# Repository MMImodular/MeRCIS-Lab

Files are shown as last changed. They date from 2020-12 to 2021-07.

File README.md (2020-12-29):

# MeRCIS Lab
##### Contributors: Matt Gaines, Joe Cressman, Jason Paximadas
___
This repository will be used to keep files up to date without dealing with Google Drive permissions.
The primary use case for now is maintaining a standard Eagle Library for future designs, but more will appear in time.

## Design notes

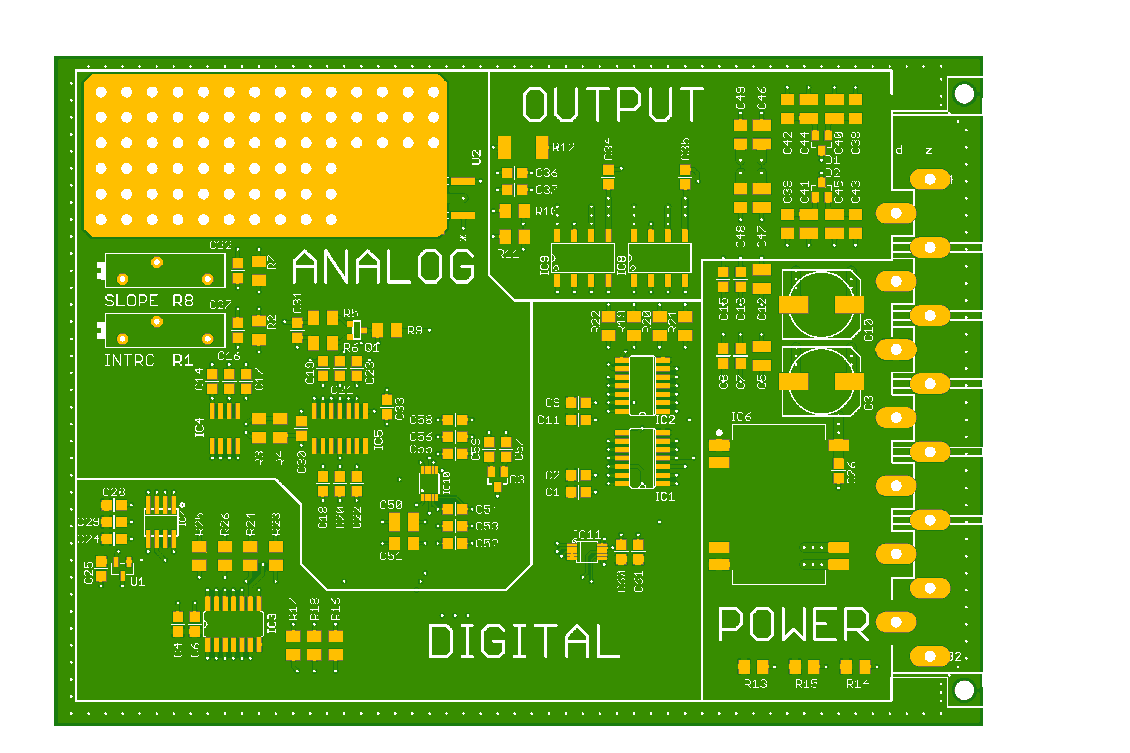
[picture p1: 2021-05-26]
Rev P/Transconductance Card222.png

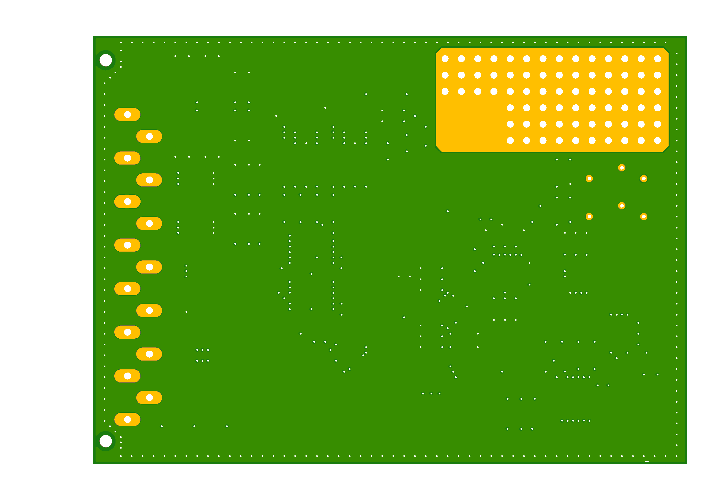
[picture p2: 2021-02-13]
Rev P/Transconductance Card Bottom.png

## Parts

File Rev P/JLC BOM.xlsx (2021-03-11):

Comment | Designator | Footprint | LCSC Part # | Column1
AD5551 | IC7 | SO-8 |  | pads good
0.01u | C14, C22, C23, C31, C33, C54, C58 | C0805 | C1710 (https://lcsc.com/product-detail/Multilayer-Ceramic-Capacitors-MLCC-SMD-SMT_SAMSUNG_CL21B103KBANNNC_10nF-103-10-50V_C1710.html/?href=jlc-SMT)
0.1u | C40, C41, C44, C45, C46, C47, C50 | C1210 | C141218
0.1u | C2, C6, C8, C11, C15, C16, C20, C21, C26, C27, C28, C30, C32, C34, C36, C53, C56, C57, C61 | C0805 | C49678 (https://lcsc.com/product-detail/Multilayer-Ceramic-Capacitors-MLCC-SMD-SMT_100nF-104-10-50V_C49678.html/?href=jlc-SMT)
100k | R2 | M1206 | C17900 (https://lcsc.com/product-detail/Chip-Resistor-Surface-Mount_Uniroyal-Elec-1206W4F1003T5E_C17900.html/?href=jlc-SMT)
100ohm | R5, R11 | M1206 | C17901 (https://lcsc.com/product-detail/Chip-Resistor-Surface-Mount_Uniroyal-Elec-1206W4F1000T5E_C17901.html/?href=jlc-SMT)
10k | R13, R14, R15, R16, R17, R18 | M1206 | C17902 (https://lcsc.com/product-detail/Chip-Resistor-Surface-Mount_Uniroyal-Elec-1206W4F1002T5E_C17902.html/?href=jlc-SMT)
10u | C5, C12 | C1210 | C39232 (https://lcsc.com/product-detail/Multilayer-Ceramic-Capacitors-MLCC-SMD-SMT_SAMSUNG_CL32B106KAJNNNE_10uF-106-10-25V_C39232.html/?href=jlc-SMT)
10u | C29 | C0805 | C15850 (https://lcsc.com/product-detail/Multilayer-Ceramic-Capacitors-MLCC-SMD-SMT_SAMSUNG_CL21A106KAYNNNE_10uF-106-10-25V_C15850.html/?href=jlc-SMT)
1k | R4, R6, R9, R10, R25 | M1206 | C4410 (https://lcsc.com/product-detail/Chip-Resistor-Surface-Mount_Uniroyal-Elec-1206W4F1001T5_C4410.html/?href=jlc-SMT)
1n | C38, C39, C42, C43, C48, C49, C51 | C1206 | C35216 (https://lcsc.com/product-detail/Multilayer-Ceramic-Capacitors-MLCC-SMD-SMT_SAMSUNG_CL31B102KGFNNNE_1nF-102-10-500V_C35216.html/?href=jlc-SMT)
1n | C35, C37, C59 | C0805 | C46653 (https://lcsc.com/product-detail/Multilayer-Ceramic-Capacitors-MLCC-SMD-SMT_SAMSUNG_CL21B102KBCNNNC_1nF-102-10-50V_C46653.html/?href=jlc-SMT)
1ohm | R12 | R2512 | C11254 (https://lcsc.com/product-detail/Chip-Resistor-Surface-Mount_Uniroyal-Elec-25121WF100KT4E_C11254.html/?href=jlc-SMT)
1u | C1, C4, C7, C9, C13, C17, C18, C19, C24, C25, C52, C55, C60 | C0805 | C28323 (https://lcsc.com/product-detail/Multilayer-Ceramic-Capacitors-MLCC-SMD-SMT_SAMSUNG_CL21B105KBFNNNE_1uF-105-10-50V_C28323.html/?href=jlc-SMT)
20k | R1 | PT-SPIN
220 | R3 | M1206 | C17957 (https://lcsc.com/product-detail/Chip-Resistor-Surface-Mount_Uniroyal-Elec-1206W4F2200T5E_C17957.html/?href=jlc-SMT)
2N7000 | Q1 | SOT-23
2k | R26 | M1206 | C17944 (https://lcsc.com/product-detail/Chip-Resistor-Surface-Mount_Uniroyal-Elec-1206W4F2001T5E_C17944.html/?href=jlc-SMT)
330 | R19, R20, R21, R22, R23, R24 | M1206 | C17930 (https://lcsc.com/product-detail/Chip-Resistor-Surface-Mount_Uniroyal-Elec-1206W4F3300T5E_C17930.html/?href=jlc-SMT)
470u | C3, C10 | 140CLH-1010 | C3350 (https://lcsc.com/product-detail/Aluminum-Electrolytic-Capacitors-SMD_Honor-Elec-RVT1V471M1010_C3350.html/?href=jlc-SMT)
5k | R8 | PT-SPIN
74LS00 | IC1, IC2 | 74XX-US_SO14:1 | C74558 | NOTE: IC2 should be replaced with the SN7438 due to sink current requirements to fully activate SSRs
74LS07D | IC3 | SO14 | C6801 (https://lcsc.com/product-detail/74-Series_TI_SN74LS07DRG4_SN74LS07DRG4_C6801.html/?href=jlc-SMT)
9.1k | R7 | M1206 | C18025 (https://lcsc.com/product-detail/Chip-Resistor-Surface-Mount_Uniroyal-Elec-1206W4F9101T5E_C18025.html/?href=jlc-SMT)
ADS8319 | IC11 | VSSOP-10 |  | pads good
ASSR-1530 | IC8, IC9 | ASSR-1530_SO8
BAS70-04 | D1, D2, D3 | SOT23 | C134375 (https://lcsc.com/product-detail/Schottky-Barrier-Diodes-SBD_DIODES_BAS70-04-7-F_BAS70-04-7-F_C134375.html/?href=jlc-SMT)
H15MLE | X1 | H15ML
IRF9Z24NPbF | U2 | UL_IRF9Z24_D2PAK | C169781
LT1991MS | IC10 | MSOP10 |  | EXTEND PADS FOR SOLDERING
MCP1700T-3302E/TT | U1 | SOT-23_MC | C39051 (https://lcsc.com/product-detail/Low-Dropout-Regulators-LDO_MICROCHIP_MCP1700T-3302E-TT_MCP1700T-3302E-TT_C39051.html/?href=jlc-SMT)
LM324D | IC5 | SO14 | C71035 (https://lcsc.com/product-detail/General-Purpose-Amplifiers_STMicroelectronics_LM324DT_LM324DT_C71035.html/?href=jlc-SMT)
SF_ISC03_DC_DC16-SMD | IC6 | SF_ISC03_SOP254P1879X863-16N
TLC272D | IC4 | SO08 | C6982 (https://lcsc.com/product-detail/General-Purpose-Amplifiers_TI_TLC272IDRG4_TLC272IDRG4_C6982.html/?href=jlc-SMT)

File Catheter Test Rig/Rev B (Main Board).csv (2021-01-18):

Qty | Value | Device | Package | Parts | Description | MF | MPN | OC_FARNELL | OC_NEWARK | POPULARITY | SPICEPREFIX | TP_SIGNAL_NAME
3 |  | 10-XX | B3F-10XX | S2, S3, S4 | OMRON SWITCH |  | B3F-1000 | 176432 | 36M3542 | 72
1 |  | 320-916 | 320-916 | S1 | TOGGLE SWITCH |  |  |  |  | 4
1 |  | ARDUINO_NANO | ARDUINO_NANO | ARDUINO_NANO1 | Arduino Nano V3.0
1 |  | HEADER-1X2 | HEADER-1X2-TH | H1
1 |  | JACK-PLUG1 | SPC4078 | J1 | DC POWER JACK |  |  | unknown | unknown | 3
1 |  | MA04-1 | MA04-1 | SV1 | PIN HEADER |  |  | unknown | unknown | 41
2 |  | MA20-1W | MA20-1W | SV2, SV3 | PIN HEADER |  |  | unknown | unknown | 0
10 |  | PINHD-1X1 | 1X01 | JP1, JP2, JP3, JP4, JP5, JP6, JP7, JP8, JP9, JP10 | PIN HEADER |  |  |  |  | 64
1 | 0.47uF | C-USC0805 | C0805 | C13 | CAPACITOR, American symbol |  |  |  |  |  | C
1 | 1.5k | R-US_R0805 | R0805 | R8 | RESISTOR, American symbol |  |  |  |  |  | R
2 | 100k | R-US_R0805 | R0805 | R5, R6 | RESISTOR, American symbol |  |  |  |  |  | R
1 | 100kB | TRIM_US-RJ9W | RJ9W | R7 | POTENTIOMETER |  |  |  |  | 1
13 | 100nF | C-USC0805 | C0805 | C1, C3, C5, C6, C7, C8, C9, C11, C12, C14, C15, C17, C19 | CAPACITOR, American symbol |  |  |  |  |  | C
5 | 10k | R-US_R0805 | R0805 | R1, R3, R4, R9, R21 | RESISTOR, American symbol |  |  |  |  |  | R
1 | 10uF | C-USC0805 | C0805 | C10 | CAPACITOR, American symbol |  |  |  |  |  | C
3 | 1k | R-US_R0805 | R0805 | R2, R13, R26 | RESISTOR, American symbol |  |  |  |  |  | R
3 | 1uF | C-USC0805 | C0805 | C2, C16, C18 | CAPACITOR, American symbol |  |  |  |  |  | C
1 | 317EMP | 317EMP | SOT223 | IC1 | Positive VOLTAGE REGULATOR |  |  |  |  | 6
18 | 330R | R-US_R0805 | R0805 | R10, R11, R12, R14, R15, R16, R17, R18, R19, R20, R22, R23, R24, R25, R27, R28, R29, R30 | RESISTOR, American symbol |  |  |  |  |  | R
1 | 330nF | C-USC0805 | C0805 | C4 | CAPACITOR, American symbol |  |  |  |  |  | C
3 | 74LVC1G14DCK | 74LVC1G14DCK | SC70-5 | IC3, IC6, IC9 | Single Schmitt-Trigger Inverter Gate |  |  |  |  | 0
1 | DCP012415DBP | DCP012415DBP | 7-PDIP | IC10
1 | HEADER-2X8-TH | HEADER-2X8-TH | HEADER-2X8-TH | H2 | SMT HEADER 2x8
1 | L78M05CDT | 7818DT | TO252 | IC2 | Positive VOLTAGE REGULATOR |  |  |  |  | 0
1 | LD1117DT33TR | 7818DT | TO252 | IC7 | Positive VOLTAGE REGULATOR |  |  |  |  | 0
2 | SN74LVC07ADR | 74LS07D | SO14 | IC5, IC8 | Hex BUFFER, open collector high-voltage output |  |  |  |  | 0
1 | TL071D | TL071D | SO08 | IC4 | OP AMP |  |  |  |  | 0
2 | TPB2,54 | TPB2,54 | B2,54 | TP1, TP2 | Test pad |  |  |  |  | 3

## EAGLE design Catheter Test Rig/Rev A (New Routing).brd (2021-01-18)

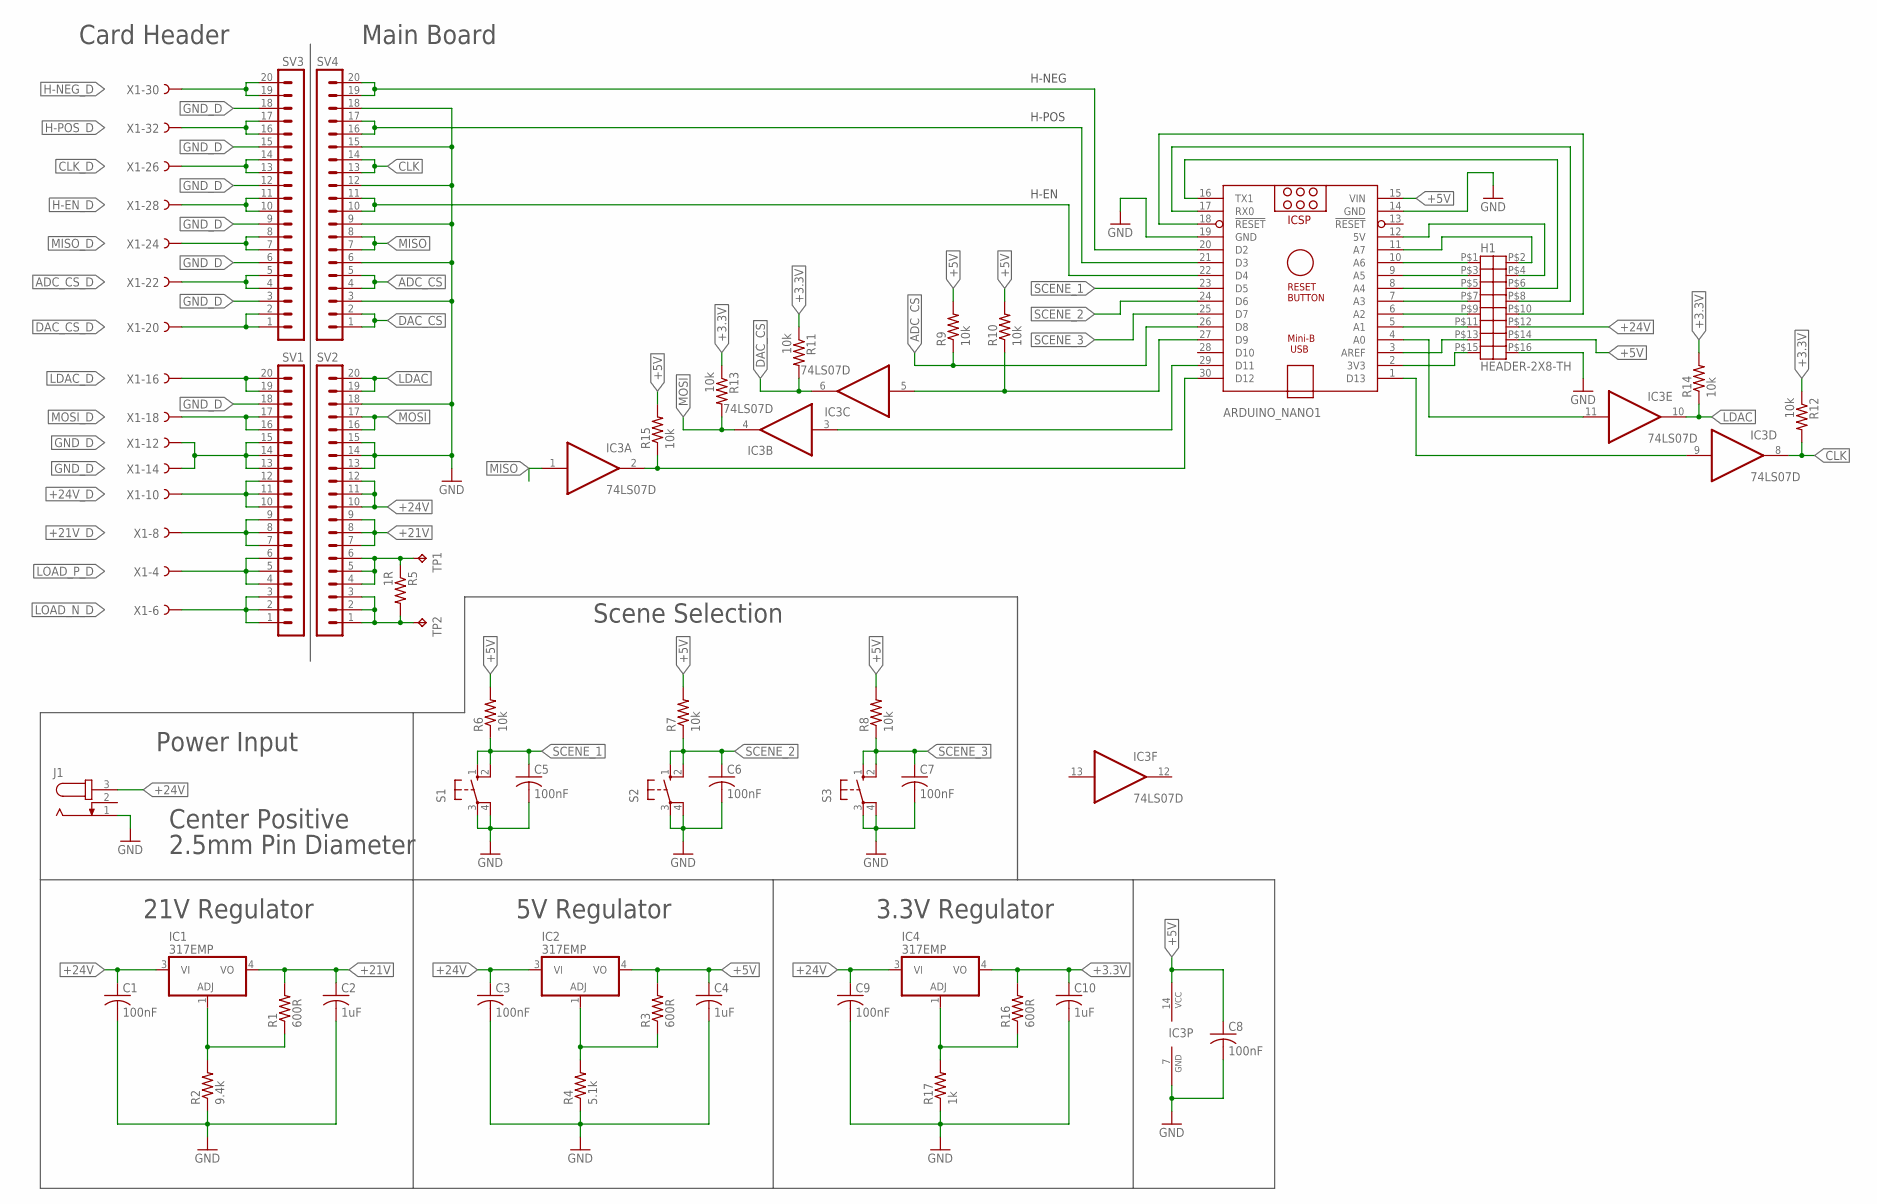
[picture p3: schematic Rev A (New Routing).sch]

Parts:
ARDUINO_NANO1: ARDUINO_NANO
C1, C3, C5, C6, C7, C8, C9: 100nF; C0603
C2, C4, C10: 1uF; C1206
H1: HEADER-2X8-TH
IC1, IC2, IC4: 317EMP; SOT223
IC3: 74LS07D; SO14
J1: JACK-PLUG1; SPC4078
R1, R3, R16: 600R; R0603
R2: 9.4k; R0603
R4: 5.1k; R0603
R5: 1R; R1206
R6, R7, R8, R9, R10, R11, R12, R13, R14, R15: 10k; R0603
R17: 1k; R0603
S1, S2, S3: 10-XX; B3F-10XX
SV1, SV3: MA20-1
SV2, SV4: MA20-1W
TP1, TP2: TPB2,54; B2,54
X1: FH15

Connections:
+3.3V: C10.1, IC4.4 (VO), R11.1, R12.1, R13.1, R14.2, R16.2
+5V: ARDUINO_NANO1.15 (VIN), C4.1, C8.1, H1.P$14, IC2.4 (VO), IC3.14 (VCC), R3.2, R6.2, R7.2, R8.2, R9.2, R10.2, R15.2
+21V: C2.1, IC1.4 (VO), R1.2, SV2.7, SV2.8, SV2.9
+21V_D: SV1.7, SV1.8, SV1.9, X1.8
+24V: C1.1, C3.1, C9.1, H1.P$12, IC1.3 (VI), IC2.3 (VI), IC4.3 (VI), J1.3, SV2.10, SV2.11, SV2.12
+24V_D: SV1.10, SV1.11, SV1.12, X1.10
ADC_CS: ARDUINO_NANO1.26 (D8), R9.1, SV4.4, SV4.5
ADC_CS_D: SV3.4, SV3.5, X1.22
CLK: IC3.8 (O), R12.2, SV4.13, SV4.14
CLK_D: SV3.13, SV3.14, X1.26
DAC_CS: IC3.6 (O), R11.2, SV4.1, SV4.2
DAC_CS_D: SV3.1, SV3.2, X1.20
GND: ARDUINO_NANO1.14 (GND), ARDUINO_NANO1.19 (GND), C1.2, C2.2, C3.2, C4.2, C5.2, C6.2, C7.2, C8.2, C9.2, C10.2, H1.P$16, IC3.7 (GND), J1.1, R2.1, R4.1, R17.1, S1.3, S1.4 (P1), S2.3, S2.4 (P1), S3.3, S3.4 (P1), SV2.13, SV2.14, SV2.15, SV2.18, SV4.3, SV4.6, SV4.9, SV4.12, SV4.15, SV4.18
GND_D: SV1.13, SV1.14, SV1.15, SV1.18, SV3.3, SV3.6, SV3.9, SV3.12, SV3.15, SV3.18, X1.12, X1.14
H-EN_D: SV3.10, SV3.11, X1.28
H-NEG_D: SV3.19, SV3.20, X1.30
H-POS_D: SV3.16, SV3.17, X1.32
LDAC: IC3.10 (O), R14.1, SV2.19, SV2.20
LDAC_D: SV1.19, SV1.20, X1.16
LOAD_N_D: SV1.1, SV1.2, SV1.3, X1.6
LOAD_P_D: SV1.4, SV1.5, SV1.6, X1.4
MISO: IC3.1 (I), SV4.7, SV4.8
MISO_D: SV3.7, SV3.8, X1.24
MOSI: IC3.4 (O), R13.2, SV2.16, SV2.17
MOSI_D: SV1.16, SV1.17, X1.18
unnamed: IC2.1 (ADJ), R3.1, R4.2
unnamed: IC1.1 (ADJ), R1.1, R2.2
unnamed: ARDUINO_NANO1.20 (D2), SV4.19, SV4.20
unnamed: ARDUINO_NANO1.2 (3V3), H1.P$15
unnamed: ARDUINO_NANO1.21 (D3), SV4.16, SV4.17
unnamed: ARDUINO_NANO1.3 (AREF), H1.P$13
unnamed: ARDUINO_NANO1.5 (A1), H1.P$11
unnamed: ARDUINO_NANO1.6 (A2), H1.P$9
unnamed: ARDUINO_NANO1.22 (D4), SV4.10, SV4.11
unnamed: ARDUINO_NANO1.7 (A3), H1.P$7
unnamed: ARDUINO_NANO1.8 (A4), H1.P$5
unnamed: ARDUINO_NANO1.9 (A5), H1.P$3
unnamed: ARDUINO_NANO1.10 (A6), H1.P$1
unnamed: ARDUINO_NANO1.11 (A7), H1.P$2
unnamed: ARDUINO_NANO1.12 (5V), H1.P$4
unnamed: ARDUINO_NANO1.16 (TX1), H1.P$6
unnamed: ARDUINO_NANO1.17 (RX0), H1.P$8
unnamed: ARDUINO_NANO1.18 (!RESET), H1.P$10
unnamed: ARDUINO_NANO1.27 (D9), IC3.5 (I), R10.1
unnamed: ARDUINO_NANO1.1 (D13), IC3.9 (I)
unnamed: ARDUINO_NANO1.29 (D11), IC3.3 (I)
unnamed: R5.1, SV2.4, SV2.5, SV2.6, TP1.TP
unnamed: R5.2, SV2.1, SV2.2, SV2.3, TP2.TP
unnamed: ARDUINO_NANO1.4 (A0), IC3.11 (I)
unnamed: ARDUINO_NANO1.30 (D12), IC3.2 (O), R15.1
unnamed: IC4.1 (ADJ), R16.1, R17.2
SCENE_1: ARDUINO_NANO1.23 (D5), C5.1, R6.1, S1.1 (S), S1.2 (S1)
SCENE_2: ARDUINO_NANO1.24 (D6), C6.1, R7.1, S2.1 (S), S2.2 (S1)
SCENE_3: ARDUINO_NANO1.25 (D7), C7.1, R8.1, S3.1 (S), S3.2 (S1)

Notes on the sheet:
Card Header
Power Input
Center Positive
2.5mm Pin Diameter
21V Regulator
Main Board
5V Regulator
Scene Selection
H-EN
H-POS
H-NEG
3.3V Regulator

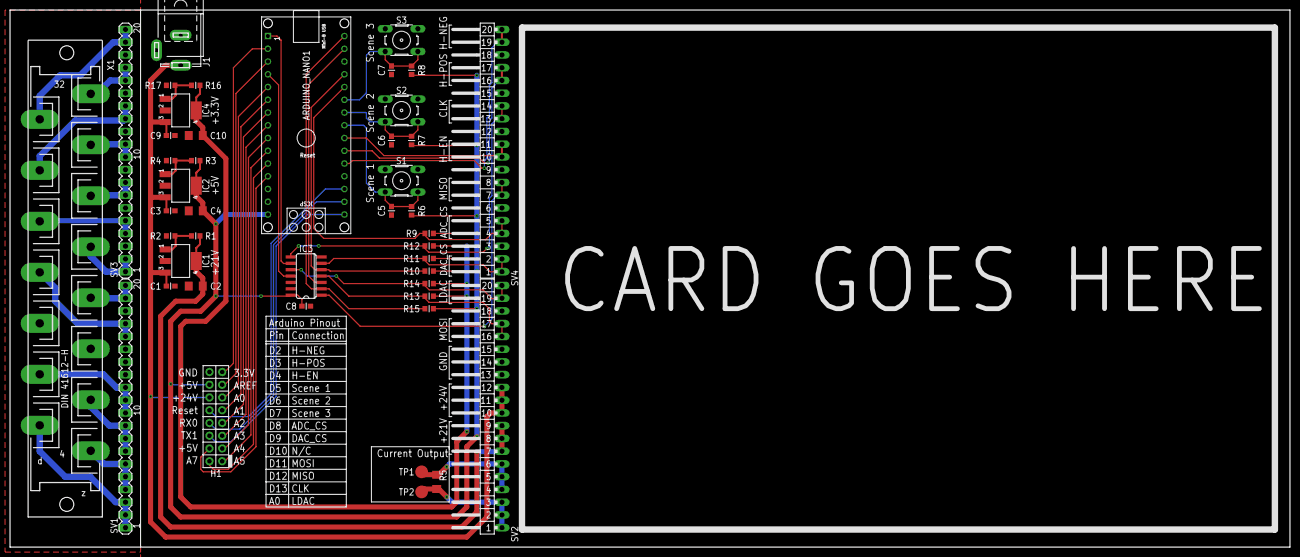
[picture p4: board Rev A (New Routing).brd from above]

Board: 2 copper layers, 255.0 x 107.0 mm, 44 parts (0 on the bottom side), 54 nets.

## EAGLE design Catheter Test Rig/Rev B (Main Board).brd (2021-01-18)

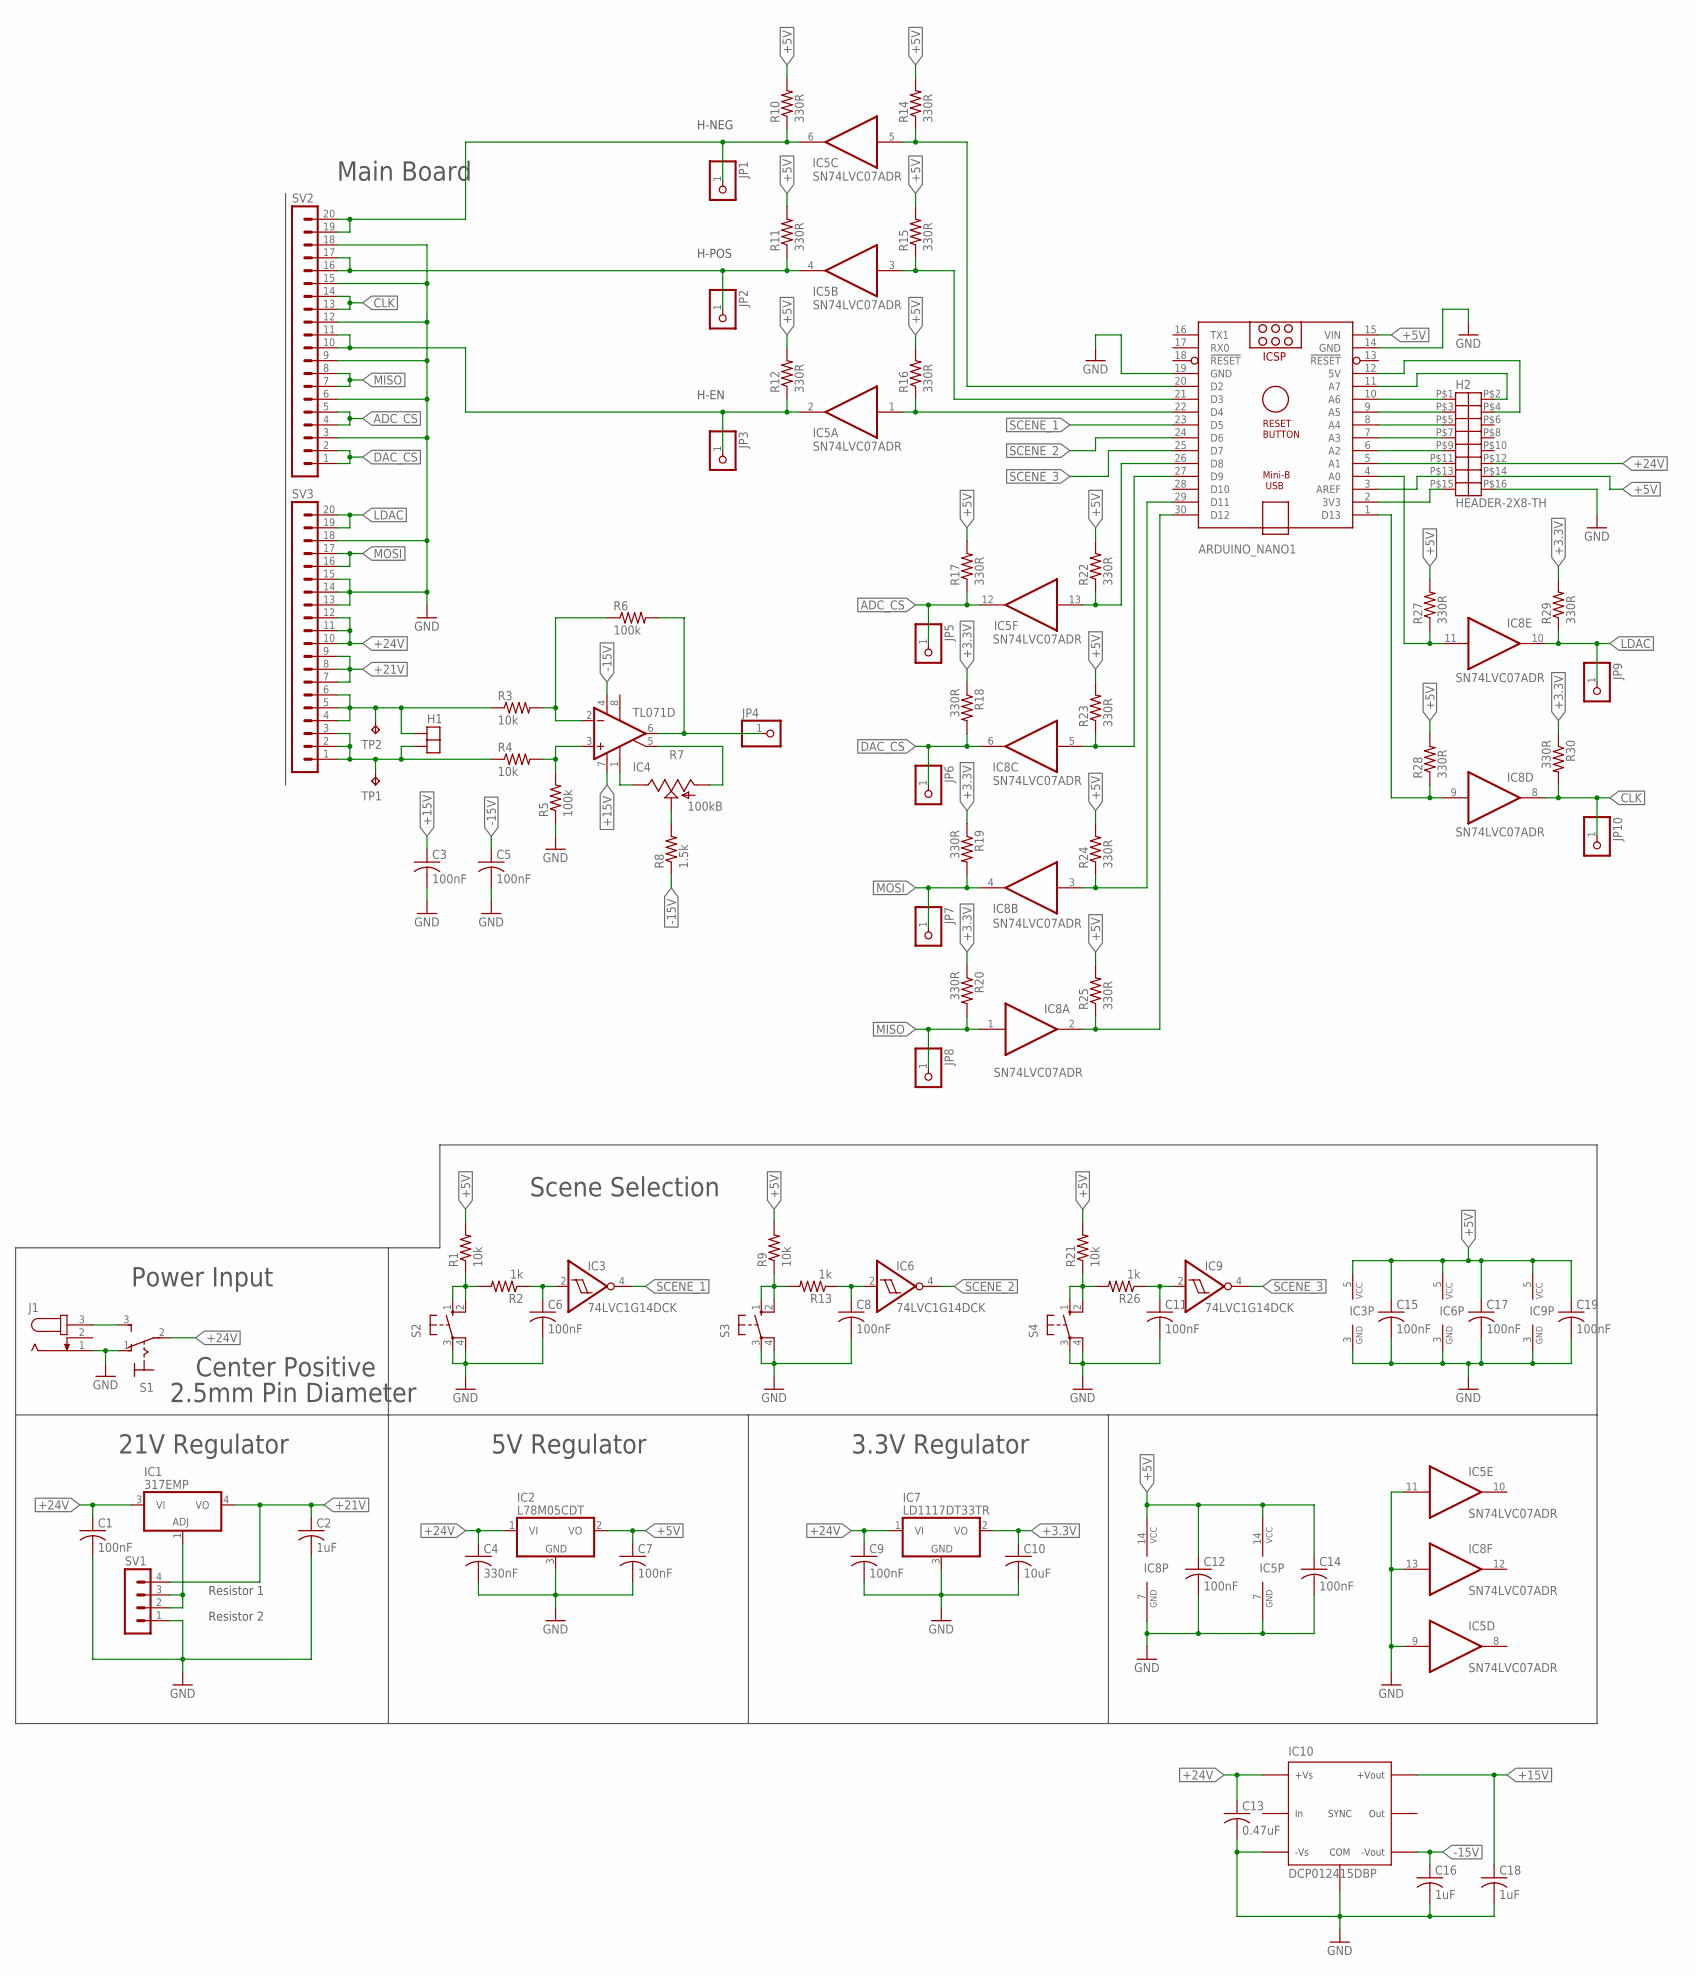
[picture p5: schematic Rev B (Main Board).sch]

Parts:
ARDUINO_NANO1: ARDUINO_NANO
C1, C3, C5, C6, C7, C8, C9, C11, C12, C14, C15, C17, C19: 100nF; C0805
C2, C16, C18: 1uF; C0805
C4: 330nF; C0805
C10: 10uF; C0805
C13: 0.47uF; C0805
H1: HEADER-1X2; HEADER-1X2-TH
H2: HEADER-2X8-TH
IC1: 317EMP; SOT223
IC2: L78M05CDT; TO252
IC3, IC6, IC9: 74LVC1G14DCK; SC70-5
IC4: TL071D; SO08
IC5, IC8: SN74LVC07ADR; SO14
IC7: LD1117DT33TR; TO252
IC10: DCP012415DBP; 7-PDIP
J1: JACK-PLUG1; SPC4078
JP1, JP2, JP3, JP4, JP5, JP6, JP7, JP8, JP9, JP10: PINHD-1X1; 1X01
R1, R3, R4, R9, R21: 10k; R0805
R2, R13, R26: 1k; R0805
R5, R6: 100k; R0805
R7: 100kB; RJ9W
R8: 1.5k; R0805
R10, R11, R12, R14, R15, R16, R17, R18, R19, R20, R22, R23, R24, R25, R27, R28, R29, R30: 330R; R0805
S1: 320-916
S2, S3, S4: 10-XX; B3F-10XX
SV1: MA04-1
SV2, SV3: MA20-1W
TP1, TP2: TPB2,54; B2,54

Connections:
+3.3V: C10.1, IC7.2 (VO), R18.1, R19.1, R20.1, R29.2, R30.1
+5V: ARDUINO_NANO1.15 (VIN), C7.1, C12.1, C14.1, C15.1, C17.1, C19.1, H2.P$14, IC2.2 (VO), IC3.5 (VCC), IC5.14 (VCC), IC6.5 (VCC), IC8.14 (VCC), IC9.5 (VCC), R1.2, R9.2, R10.2, R11.2, R12.2, R14.2, R15.2, R16.2, R17.2, R21.2, R22.2, R23.2, R24.2, R25.2, R27.2, R28.2
+15V: C3.1, C18.1, IC4.7 (V+), IC10.P$4
+21V: C2.1, IC1.4 (VO), SV1.4, SV3.7, SV3.8, SV3.9
+24V: C1.1, C4.1, C9.1, C13.1, H2.P$12, IC1.3 (VI), IC2.1 (VI), IC7.1 (VI), IC10.P$1, S1.2, SV3.10, SV3.11, SV3.12
-15V: C5.1, C16.1, IC4.4 (V-), IC10.P$5, R8.1
ADC_CS: IC5.12 (O), JP5.1, R17.1, SV2.4, SV2.5
CLK: IC8.8 (O), JP10.1, R30.2, SV2.13, SV2.14
DAC_CS: IC8.6 (O), JP6.1, R18.2, SV2.1, SV2.2
GND: ARDUINO_NANO1.14 (GND), ARDUINO_NANO1.19 (GND), C1.2, C2.2, C3.2, C4.2, C5.2, C6.2, C7.2, C8.2, C9.2, C10.2, C11.2, C12.2, C13.2, C14.2, C15.2, C16.2, C17.2, C18.2, C19.2, H2.P$16, IC2.3 (GND), IC3.3 (GND), IC5.7 (GND), IC5.9 (I), IC5.11 (I), IC6.3 (GND), IC7.3 (GND), IC8.7 (GND), IC8.13 (I), IC9.3 (GND), IC10.P$2, IC10.P$3, J1.1, R5.1, S1.1 (O), S2.3, S2.4 (P1), S3.3, S3.4 (P1), S4.3, S4.4 (P1), SV1.1, SV2.3, SV2.6, SV2.9, SV2.12, SV2.15, SV2.18, SV3.13, SV3.14, SV3.15, SV3.18
LDAC: IC8.10 (O), JP9.1, R29.1, SV3.19, SV3.20
MISO: IC8.1 (I), JP8.1, R20.2, SV2.7, SV2.8
MOSI: IC8.4 (O), JP7.1, R19.2, SV3.16, SV3.17
unnamed: IC5.2 (O), JP3.1, R12.1, SV2.10, SV2.11
unnamed: IC4.2 (-IN), R3.2, R6.1
unnamed: J1.3, S1.3 (S)
unnamed: ARDUINO_NANO1.2 (3V3), H2.P$15
unnamed: ARDUINO_NANO1.21 (D3), IC5.3 (I), R15.1
unnamed: ARDUINO_NANO1.3 (AREF), H2.P$13
unnamed: ARDUINO_NANO1.5 (A1), H2.P$11
unnamed: ARDUINO_NANO1.6 (A2), H2.P$9
unnamed: ARDUINO_NANO1.22 (D4), IC5.1 (I), R16.1
unnamed: ARDUINO_NANO1.7 (A3), H2.P$7
unnamed: ARDUINO_NANO1.8 (A4), H2.P$5
unnamed: ARDUINO_NANO1.9 (A5), H2.P$3
unnamed: ARDUINO_NANO1.10 (A6), H2.P$1
unnamed: ARDUINO_NANO1.11 (A7), H2.P$2
unnamed: ARDUINO_NANO1.12 (5V), H2.P$4
unnamed: ARDUINO_NANO1.27 (D9), IC8.5 (I), R23.1
unnamed: ARDUINO_NANO1.1 (D13), IC8.9 (I), R28.1
unnamed: ARDUINO_NANO1.29 (D11), IC8.3 (I), R24.1
unnamed: H1.P$1, R3.1, SV3.4, SV3.5, SV3.6, TP2.TP
unnamed: H1.P$2, R4.1, SV3.1, SV3.2, SV3.3, TP1.TP
unnamed: ARDUINO_NANO1.4 (A0), IC8.11 (I), R27.1
unnamed: ARDUINO_NANO1.30 (D12), IC8.2 (O), R25.1
unnamed: IC5.4 (O), JP2.1, R11.1, SV2.16, SV2.17
unnamed: R1.1, R2.2, S2.1 (S), S2.2 (S1)
unnamed: C6.1, IC3.2 (I), R2.1
unnamed: R9.1, R13.2, S3.1 (S), S3.2 (S1)
unnamed: C8.1, IC6.2 (I), R13.1
unnamed: R21.1, R26.2, S4.1 (S), S4.2 (S1)
unnamed: C11.1, IC9.2 (I), R26.1
unnamed: IC1.1 (ADJ), SV1.2, SV1.3
unnamed: ARDUINO_NANO1.20 (D2), IC5.5 (I), R14.1
unnamed: ARDUINO_NANO1.26 (D8), IC5.13 (I), R22.1
unnamed: IC5.6 (O), JP1.1, R10.1, SV2.19, SV2.20
unnamed: IC4.3 (+IN), R4.2, R5.2
unnamed: IC4.6 (OUT), JP4.1, R6.2
unnamed: IC4.1 (ON1), R7.E
unnamed: IC4.5 (ON2), R7.A
unnamed: R7.S, R8.2
SCENE_1: ARDUINO_NANO1.23 (D5), IC3.4 (O)
SCENE_2: ARDUINO_NANO1.24 (D6), IC6.4 (O)
SCENE_3: ARDUINO_NANO1.25 (D7), IC9.4 (O)

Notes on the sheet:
Power Input
Center Positive
2.5mm Pin Diameter
21V Regulator
Main Board
5V Regulator
Scene Selection
H-EN
H-POS
H-NEG
3.3V Regulator
Resistor 1
Resistor 2

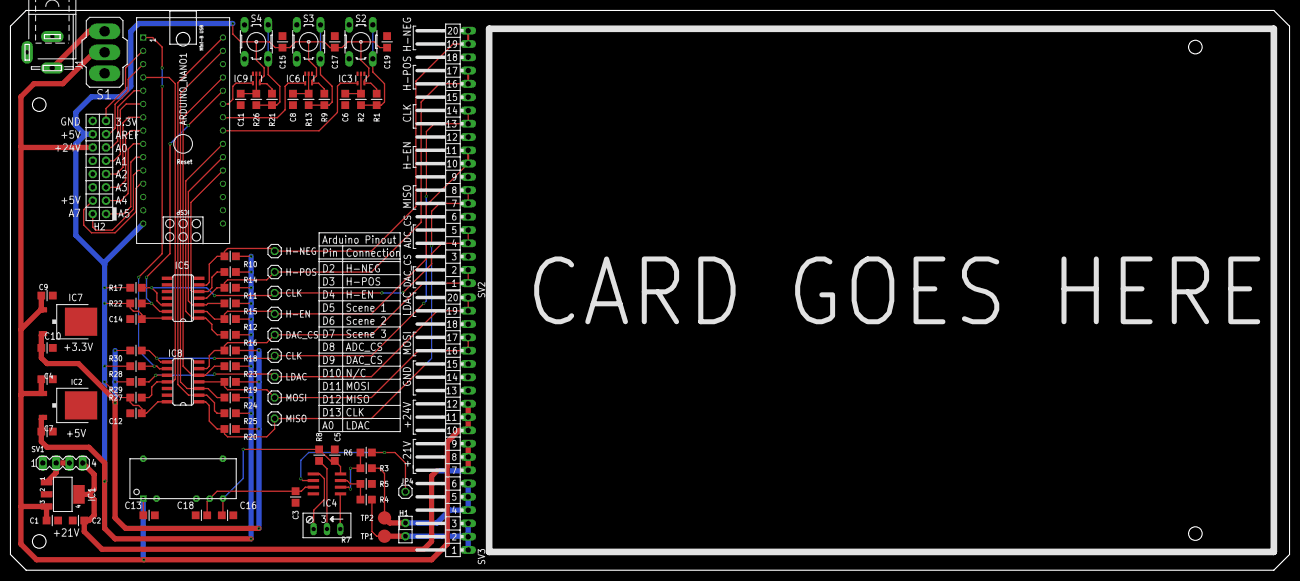
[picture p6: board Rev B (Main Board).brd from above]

Board: 2 copper layers, 244.5 x 107.0 mm, 82 parts (0 on the bottom side), 54 nets.

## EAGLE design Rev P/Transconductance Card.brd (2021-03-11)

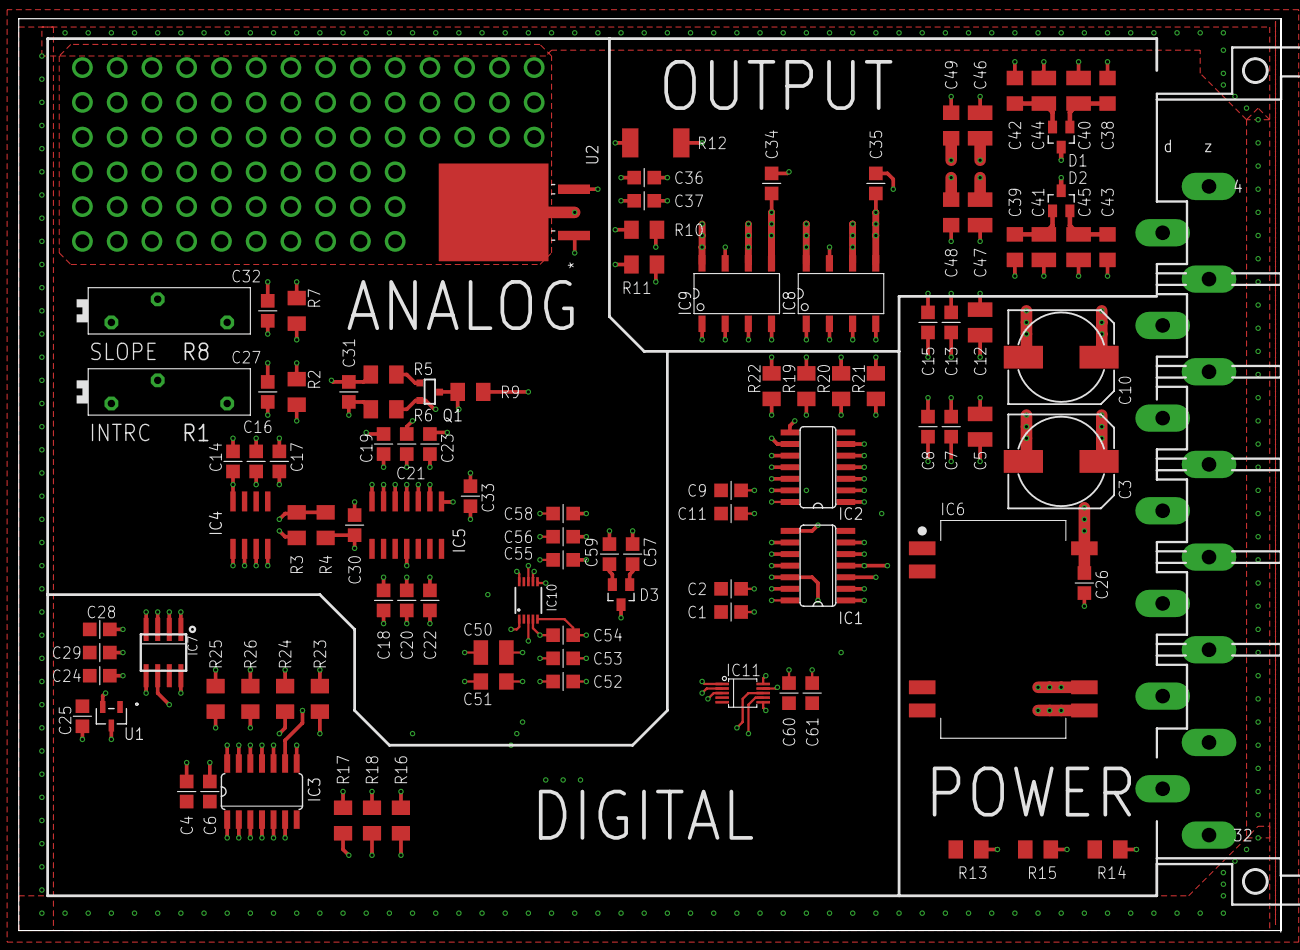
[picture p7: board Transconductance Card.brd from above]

Board: 4 copper layers, 138.4 x 100.0 mm, 105 parts (0 on the bottom side), 58 nets.

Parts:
C1, C4, C7, C9, C13, C17, C18, C19, C24, C25, C52, C55, C60: 1u; C0805
C2, C6, C8, C11, C15, C16, C20, C21, C26, C27, C28, C30, C32, C34, C36, C53, C56, C57, C61: 0.1u; C0805
C3, C10: 470u; 140CLH-1010
C5, C12: 10u; C1210
C14, C22, C23, C31, C33, C54, C58: 0.01u; C0805
C29: 10u; C0805
C35, C37, C59: 1n; C0805
C38, C39, C42, C43, C48, C49, C51: 1n; C1206
C40, C41, C44, C45, C46, C47, C50: 0.1u; C1210
D1, D2, D3: BAS70-04; SOT23
IC1, IC2: 74LS00; 74XX-US_SO14:1
IC3: 74LS07D; SO14
IC4: TLC272D; SO08
IC5: OP484; SO14
IC6: SF_ISC03_DC_DC16-SMD; SF_ISC03_SOP254P1879X863-16N
IC7: SO-8
IC8, IC9: ASSR-1530; ASSR-1530_SO8
IC10: LT1991MS; MSOP10
IC11: ADS8319; VSSOP-10
Q1: 2N7000; SOT-23
R1: 20k; PT-SPIN
R2: 100k; M1206
R3: 220; M1206
R4, R6, R9, R10, R25: 1k; M1206
R5, R11: 100ohm; M1206
R7: 9.1k; M1206
R8: 5k; PT-SPIN
R12: 1ohm; R2512
R13, R14, R15, R16, R17, R18: 10k; M1206
R19, R20, R21, R22, R23, R24: 330; M1206
R26: 2k; M1206
U1: MCP1700T-3302E/TT; SOT-23_MC
U2: IRF9Z24NPbF; UL_IRF9Z24_D2PAK
X1: H15MLE; H15ML

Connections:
1: IC1.4, IC1.5, IC1.9, IC3.6, R17.2
2: IC1.1, IC1.2, IC1.13, IC3.4, R18.2
3: IC1.10, IC1.12, IC2.9, IC2.12, IC3.2, R16.2
3&1: IC8.2, R20.1
3&2: IC8.4, R21.1
+3.3V: C24.1, C28.1, C29.1, IC7.P$3, IC7.P$8, R26.1, U1.2
+5V: C1.1, C2.1, C4.1, C6.1, C9.1, C11.1, C14.1, C16.1, C17.1, C25.1, C60.1, C61.1, IC1.14, IC2.14, IC3.14, IC4.8, IC6.9, IC8.1, IC8.3, IC9.1, IC9.3, IC11.1, IC11.2, IC11.9, IC11.10, R1.1, R16.1, R17.1, R18.1, R23.2, R24.2, R25.1, U1.3
+20V: C10.+, C12.1, C13.1, C15.1, C50.1, C51.1, IC10.1, IC10.3, R9.2, R12.2, X1.Z8
+24V: C3.+, C5.1, C7.1, C8.1, C18.1, C20.1, C22.1, C26.1, C55.1, C56.1, C58.1, IC5.4, IC6.16, IC10.7, X1.D10
-5V: C19.2, C21.2, C23.2, C27.2, C52.2, C53.2, C54.2, IC5.11, IC6.10, IC10.4, R1.2
ADC-CS: IC3.9, X1.D22
AGND: C3.-, C5.2, C7.2, C8.2, C10.-, C12.2, C13.2, C14.2, C15.2, C16.2, C17.2, C18.2, C19.1, C20.2, C21.1, C22.2, C23.1, C26.2, C30.2, C32.2, C34.2, C35.2, C36.2, C37.2, C38.2, C39.2, C40.2, C41.2, C42.2, C43.2, C44.2, C45.2, C46.2, C47.2, C48.2, C49.2, C50.2, C51.2, C52.1, C53.1, C54.1, C55.2, C56.2, C57.2, C58.2, C59.2, IC4.4, IC7.P$2, IC8.7, IC9.7, IC10.5, R8.1, X1.Z12
CLK: IC3.11, IC7.P$5, X1.D26
DAC-CS: IC7.P$4, X1.Z20
DGND: C1.2, C2.2, C4.2, C6.2, C9.2, C11.2, C24.2, C25.2, C28.2, C29.2, C60.2, C61.2, IC1.7, IC2.7, IC3.7, IC6.1, IC6.8, IC7.P$7, IC11.4, IC11.5, R13.1, R14.1, R15.1, U1.1, X1.D14
H-BDG: C34.1, C35.1, IC8.5, IC9.5, U2.2
H-EN: IC3.1, R13.2, X1.Z28
H-NEG: IC3.3, R15.2, X1.D30
H-POS: IC3.5, R14.2, X1.Z32
LOAD_N: C47.1, C48.1, D2.3, IC8.6, IC8.8, X1.D6
LOAD_P: C46.1, C49.1, D1.3, IC9.6, IC9.8, X1.Z4
LSENSE: C36.1, C37.1, IC10.8, IC10.10, R10.2, R12.1, U2.3
MISO: IC3.12, R26.2, X1.Z24
MOSI: IC7.P$6, X1.D18
unnamed: D3.3, IC10.6, IC11.3
unnamed: Q1.2, R6.1, R7.2
unnamed: IC3.8, IC11.6, R23.1
unnamed: IC3.10, IC11.8, R24.1
unnamed: Q1.1, R5.1
unnamed: IC1.6, IC2.10
unnamed: IC1.3, IC2.13
unnamed: IC3.13, IC11.7, R25.2
unnamed: C31.1, IC5.14, R5.2
unnamed: IC4.3, IC7.P$1
unnamed: IC5.10, Q1.3, R9.1
unnamed: R11.2, U2.1
unnamed: C31.2, IC5.13, R6.2
unnamed: C33.2, IC5.8, R11.1
unnamed: C38.1, C40.1, D1.1
unnamed: C30.1, IC5.12, R4.2
unnamed: C32.1, R7.1, R8.2, R8.3
unnamed: C33.1, IC5.9, R10.1
unnamed: C27.1, R1.3, R2.1
unnamed: C42.1, C44.1, D1.2
unnamed: IC1.8, IC2.4, IC2.5
unnamed: IC1.11, IC2.1, IC2.2
unnamed: IC2.8, R19.2
unnamed: IC2.6, R20.2
unnamed: IC2.3, R21.2
unnamed: IC4.1, R3.2, R4.1
unnamed: IC2.11, R22.2
unnamed: C39.1, C41.1, D2.1
unnamed: C43.1, C45.1, D2.2
unnamed: C57.1, D3.1
unnamed: C59.1, D3.2
unnamed: IC4.2, R2.2, R3.1
~3||1: IC9.4, R19.1
~3||2: IC9.2, R22.1

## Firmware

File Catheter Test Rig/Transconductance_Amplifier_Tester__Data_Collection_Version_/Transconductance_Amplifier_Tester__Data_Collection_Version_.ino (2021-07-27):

/*
This code is designed to run on an Arduino Nano Every with the transconductance card tester
*/ 
#include <SPI.h>
#define L_DAC A0

//Pin Definitions
const int DAC_CS = 9;
const int H_NEG = 2;
const int H_POS = 3;
const int H_EN = 4;
const int ADC_CS = 8;
const int button1 = 5;
const int button2 = 6;
const int button3 = 7;

//Dac Max Value
const int dacMax14 = 16383; //14 bit maximum value
const int dacMax12 = 4095; //12 bit maximum value
int dacMax = dacMax14;

//Variables
int dacOut = 0;
uint16_t sense;
float tx;
int sceneCounter1 = 0;
int sceneCounter2 = 0;
int sceneCounter3 = 0;
int currentScene = 1;

//Boolean Checks
bool dac14 = true; //used to determine which DAC is present (true = 14 bit, false = 12 bit)
bool sc1Change = false;
bool sc2Change = false;
bool sc3Change = false;
bool firstTime = true;

//Need to configure ADC such that it is slower than the DAC.
//It cannot read very fast.
SPISettings DAC_SETTINGS = SPISettings(1000000, MSBFIRST, SPI_MODE0);
SPISettings ADC_SETTINGS = SPISettings(125000, MSBFIRST, SPI_MODE0);

//Setup----------------------------------------------------------------------------------------------------------------------------------------
void setup() {
  
  //Set up SPI
  Serial.begin(4800);
  SPI.begin(); 

  //Configure DAC_CS pin
  pinMode (DAC_CS, OUTPUT);
  
  //Configure ADC_CS pin
  pinMode (ADC_CS, OUTPUT);
  
  //Configure H Bridge
  pinMode (H_NEG, OUTPUT);
  pinMode (H_POS, OUTPUT);
  pinMode (H_EN, OUTPUT);
  
  //Car no go if this pin isn't held low
  pinMode (L_DAC, OUTPUT);
  
  digitalWrite(H_POS, LOW); //Pull both ends low to start
  digitalWrite(H_NEG, LOW);
  digitalWrite(H_EN, HIGH); //Ensure H-Bridge is always active
  digitalWrite(L_DAC, LOW);

  //Create interrupts for scene selection
  attachInterrupt(digitalPinToInterrupt(button1), incSC1, FALLING);
  attachInterrupt(digitalPinToInterrupt(button2), incSC2, FALLING);
  attachInterrupt(digitalPinToInterrupt(button3), dacSelect, FALLING);
}

//Begin Loop ---------------------------------------------------------------------------------------------------------------------------------
void loop() {
  /*
    setDirection(true);
    //rising
    setDac(dacMax);
    delay(5000);
    //falling
    setDac(0);
    delay(5000);

  //ugly if else that works
    //Triangle functions for Scene 1
    if(sceneCounter1 == 0 && sc1Change == true) {
      fastTriangle();
    }
    if(sceneCounter1 == 1 && sc1Change == true) {
      posTriangle();
    }
    if(sceneCounter1 == 2 && sc1Change == true) {
      negTriangle();
    }
    if(sceneCounter1 == 3 && sc1Change == true) {
      biTriangle();
    }

    //PWM functions for Scene 2
    if(sceneCounter2 == 0 && sc2Change == true) { //patch for output staying maxed out when SC2 = 0
      setDac(0);
    }
    if(sceneCounter2 == 1 && sc2Change == true) {
      
      PWM50();
    }
    if(sceneCounter2 == 2 && sc2Change == true) {
      PWM25();
    }
    if(sceneCounter2 == 3 && sc2Change == true) {
      PWM10();
    }
    */

  //Gonna try switch cases here
  //First switch is used to determine the scene which is currently active
  //This is to differentiate between sets of functions
  switch (currentScene) {
    
    //First case is for Scene 1, featuring triangle outputs
    //This is helpful for checking nonlinearity behavior
    case 1:
      switch (sceneCounter1) {
        case 0:
          fastTriangle();
          break;
        case 1:
          posTriangle();
          break;
        case 2:
          negTriangle();
          break;
        case 3:
          biTriangle();
          break;
        default:
          setDac(0);
          break;
      }
    
    //Second case is for Scene 2, featuring various PWM functions
    //These are helpful for determining rise/fall times as well as time delay between DAC and amp output
    case 2:
      switch (sceneCounter2) {
        case 0:
          setDac(0);
          break;
        case 1:
          PWM50();
          break;
        case 2:
          PWM25();
          break;
        case 3:
          PWM10();
          break;
        default:
          setDac(0);
          break;
      }
  }
  
  //firstTime is used to check if the chosen function is running for the first time since a button has been pressed 
  //Must be reset every main loop so it is only True after interrupt
  firstTime = false; 
}
//End Loop ----------------------------------------------------------------------------------------------------------------------------------

//Interrupts---------------------------------------------------------------------------------------------------------------------------------
void incSC1() {
  sceneCounter1++;
  currentScene = 1;
  //sc1Change = true;
  //sc2Change = false;
  //sc3Change = false;
  
  firstTime = true;
  if(sceneCounter1 > 3) {
    sceneCounter1 = 0;
  }
}

void incSC2() {
  sceneCounter2++;
  currentScene = 2;
  //sc1Change = false;
  //sc2Change = true;
  //sc3Change = false;
  
  firstTime = true;
  if(sceneCounter2 > 3) {
    sceneCounter2 = 0;
  }
}

void dacSelect() {
  dac14 = !dac14;
  if (dac14 == true) {
    dacMax = dacMax14;
  }
  else {
    dacMax = dacMax12;
  }
}

//DAC write function------------------------------------------------------------------------------------------------------------------------
void setDac(int value) {
  //Convert integer to unsigned 16 bit value (Maximum of 14 bits actually used)
  uint16_t dacPrimaryByte = value;
  
  //if using the 12 bit DAC you must alter the primary byte a bit
  if(dac14 == false) {
    dacPrimaryByte &= 0x0FFF; //limit scope of data to 12 bits
    dacPrimaryByte |= 0x3000; //apply necessary setup bits for the DAC
  }
  
  //Send data to the DAC
  SPI.beginTransaction(DAC_SETTINGS);
  noInterrupts();
  digitalWrite(DAC_CS, LOW);
  SPI.transfer16(dacPrimaryByte);
  digitalWrite(DAC_CS, HIGH);
  interrupts();
  SPI.endTransaction();
}

//ADC read function-------------------------------------------------------------------------------------------------------------------------
//Need to update this to work with 16 bit ADC
float ADC_read() {
  SPI.beginTransaction(ADC_SETTINGS);
  digitalWrite(ADC_CS, LOW);
  uint16_t ret1(SPI.transfer16(0x0000));
  digitalWrite(ADC_CS, HIGH);
  SPI.endTransaction();
  sense = ret1 & 0b0001111111111111;
  tx = float(sense)/5397 * 3.3;
  return tx;
}

//Output Direction Function-----------------------------------------------------------------------------------------------------------------
void setDirection(bool direction) {
  //True = forwards
  //False = backwards
  //Close both sides of H-Bridge
  digitalWrite(H_POS, LOW);
  digitalWrite(H_NEG, LOW);
  //Short pause to eliminate shoot-through
  delay(1);
  //Enable desired direction
  if (direction == true) {
    digitalWrite(H_POS, HIGH);
  }
  if (direction == false) {
    digitalWrite(H_NEG, HIGH);
  }
}

//Triangle Wave Functions------------------------------------------------------------------------------------------------------------------
//Creates a symmetrical Triangle wave with positive current
void posTriangle() {
   setDirection(true);
    //rising
    while(dacOut < dacMax) {
      setDac(dacOut);
      dacOut++;
    }
    //falling
    while(dacOut > 0) {
      setDac(dacOut);
      dacOut--;
    }
    //make sure loop ends at 0
    dacOut = 0;
}

//Creates a symmetrical Triangle wave with negative current
void negTriangle() {
  setDirection(false);
    //rising
    while(dacOut < dacMax) {
      setDac(dacOut);
      dacOut++;
    }
    //falling
    while(dacOut > 0) {
      setDac(dacOut);
      dacOut--;
    }
  //make sure loop ends at 0
  dacOut = 0;
}

//Creates a symmetrical Triangle wave with positive and negative current
//Zero crossing will have some delay to prevent shoot-through
void biTriangle() {
  posTriangle();
  negTriangle();
}

void fastTriangle() {
  if (firstTime == true) {
    setDirection(true);
  }
  //rising
  while(dacOut < dacMax-8) {
    setDac(dacOut);
    dacOut=dacOut+8;
  }
  //falling
  while(dacOut > 8) {
    setDac(dacOut);
    dacOut=dacOut-8;
  }
  //make sure loop ends at 0
  dacOut = 0;
}
//PWM Functions----------------------------------------------------------------------------------------------------------------------------
void PWM50() {
  if (firstTime == true) {
    setDirection(true);
  }
  setDac(0);
  delay(50);
  setDac(4095);
  delay(50);
}

void PWM25() {
  if (firstTime == true) {
    setDirection(true);
  }
  setDac(0);
  delay(75);
  setDac(4095);
  delay(25);
}

void PWM10() {
  if (firstTime == true) {
    setDirection(true);
  }
  setDac(0);
  delay(90);
  setDac(4095);
  delay(10);
}

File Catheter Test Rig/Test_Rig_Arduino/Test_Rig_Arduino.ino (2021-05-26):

/*
This code is designed to run on an Arduino Nano Every with the transconductance card tester
*/ 
#include <SPI.h>
#define L_DAC A0

//Pin Definitions
const int DAC_CS = 9;
const int H_NEG = 2;
const int H_POS = 3;
const int H_EN = 4;
const int ADC_CS = 8;
const int scene1 = 5;
const int scene2 = 6;
const int scene3 = 7;

//Dac Max Value
const int dacMax = 16383; //14 bit maximum value

//Variables
int dacOut = 0;
uint16_t sense;
float tx;
int sceneCounter1 = 0;
int sceneCounter2 = 0;
int sceneCounter3 = 0;
int sinCounter = 0;

//Boolean Checks
bool sc1Change = false;
bool sc2Change = false;
bool sc3Change = false;
bool firstTime = true;

//Need to configure ADC such that it is slower than the DAC.
//It cannot read very fast.
SPISettings DAC_SETTINGS = SPISettings(1000000, MSBFIRST, SPI_MODE0);
SPISettings ADC_SETTINGS = SPISettings(125000, MSBFIRST, SPI_MODE0);

//Sine wave lookup table
int sine256[]  = {
 127,130,133,136,139,143,146,149,152,155,158,161,164,167,170,173,176,178,181,184,187,190,192,195,198,200,203,205,208,210,212,215,217,219,221,223,225,227,229,231,233,234,236,238,239,240,
 242,243,244,245,247,248,249,249,250,251,252,252,253,253,253,254,254,254,254,254,254,254,253,253,253,252,252,251,250,249,249,248,247,245,244,243,242,240,239,238,236,234,233,231,229,227,225,223,
 221,219,217,215,212,210,208,205,203,200,198,195,192,190,187,184,181,178,176,173,170,167,164,161,158,155,152,149,146,143,139,136,133,130,127,124,121,118,115,111,108,105,102,99,96,93,90,87,84,81,78,
 76,73,70,67,64,62,59,56,54,51,49,46,44,42,39,37,35,33,31,29,27,25,23,21,20,18,16,15,14,12,11,10,9,7,6,5,5,4,3,2,2,1,1,1,0,0,0,0,0,0,0,1,1,1,2,2,3,4,5,5,6,7,9,10,11,12,14,15,16,18,20,21,23,25,27,29,31,
 33,35,37,39,42,44,46,49,51,54,56,59,62,64,67,70,73,76,78,81,84,87,90,93,96,99,102,105,108,111,115,118,121,124
};

//Setup----------------------------------------------------------------------------------------------------------------------------------------
void setup() {
  
  //Set up SPI
  Serial.begin(4800);
  SPI.begin(); 

  //Configure DAC_CS pin
  pinMode (DAC_CS, OUTPUT);
  
  //Configure ADC_CS pin
  pinMode (ADC_CS, OUTPUT);
  
  //Configure H Bridge
  pinMode (H_NEG, OUTPUT);
  pinMode (H_POS, OUTPUT);
  pinMode (H_EN, OUTPUT);
  
  //Car no go if this pin isn't held low
  pinMode (L_DAC, OUTPUT);
  
  digitalWrite(H_POS, LOW); //Pull both ends low to start
  digitalWrite(H_NEG, LOW);
  digitalWrite(H_EN, HIGH); //Ensure H-Bridge is always active
  digitalWrite(L_DAC, LOW);

  //Create interrupts for scene selection
  //attachInterrupt(digitalPinToInterrupt(scene1), incSC1, FALLING);
  //attachInterrupt(digitalPinToInterrupt(scene2), incSC2, FALLING);
  //attachInterrupt(digitalPinToInterrupt(scene3), incSC3, FALLING);
}

//Begin Loop ---------------------------------------------------------------------------------------------------------------------------------
void loop() {

  setDirection(true);
    //rising
    setDac(dacMax);
    delay(5000);
    //falling
    setDac(0);
    delay(5000);
  
}
    
    /*
    //Triangle functions for Scene 1
    if(sceneCounter1 == 0 && sc1Change == true) {
      fastTriangle();
    }
    if(sceneCounter1 == 1 && sc1Change == true) {
      posTriangle();
    }
    if(sceneCounter1 == 2 && sc1Change == true) {
      negTriangle();
    }
    if(sceneCounter1 == 3 && sc1Change == true) {
      biTriangle();
    }

    //PWM functions for Scene 2
    if(sceneCounter2 == 0 && sc2Change == true) { //patch for output staying maxed out when SC2 = 0
      setDac(0);
    }
    if(sceneCounter2 == 1 && sc2Change == true) {
      
      PWM50();
    }
    if(sceneCounter2 == 2 && sc2Change == true) {
      PWM25();
    }
    if(sceneCounter2 == 3 && sc2Change == true) {
      PWM10();
    }

    //SIN function on Scene 3
    if(sceneCounter3 == 1 && sc3Change == true) { 
      sinePos();
    }
    firstTime = false; //Used to check if cycle is running for the first time since button has been pressed, reset every main loop so it is only True after interrupt

    */
//}
//End Loop ----------------------------------------------------------------------------------------------------------------------------------

//Interrupts---------------------------------------------------------------------------------------------------------------------------------
void incSC1() {
  sceneCounter1++;
  sc1Change = true;
  sc2Change = false;
  sc3Change = false;
  firstTime = true;
  if(sceneCounter1 > 3) {
    sceneCounter1 = 0;
  }
}

void incSC2() {
  sceneCounter2++;
  sc1Change = false;
  sc2Change = true;
  sc3Change = false;
  firstTime = true;
  if(sceneCounter2 > 3) {
    sceneCounter2 = 0;
  }
}

void incSC3() {
  sceneCounter3++;
  sc1Change = false;
  sc2Change = false;
  sc3Change = true;
  firstTime = true;
  if(sceneCounter3 > 3) {
    sceneCounter3 = 0;
  }
}

//DAC write function------------------------------------------------------------------------------------------------------------------------
void setDac(int value) {
  
  //Convert integer to unsigned 16 bit value (only 14 bits actually used)
  uint16_t dacPrimaryByte = value;
  //Send data
  noInterrupts();
  digitalWrite(DAC_CS, LOW);
  SPI.transfer16(dacPrimaryByte);
  digitalWrite(DAC_CS, HIGH);
  interrupts();
}

//ADC read function-------------------------------------------------------------------------------------------------------------------------
//Need to update this to work with 16 bit ADC
float ADC_read() {
  SPI.beginTransaction(ADC_SETTINGS);
  digitalWrite(ADC_CS, LOW);
  uint16_t ret1(SPI.transfer16(0x0000));
  digitalWrite(ADC_CS, HIGH);
  SPI.endTransaction();
  sense = ret1 & 0b0001111111111111;
  tx = float(sense)/5397 * 3.3;
  return tx;
}

//Output Direction Function-----------------------------------------------------------------------------------------------------------------
void setDirection(bool direction) {
  //True = forwards
  //False = backwards
  //Close both sides of H-Bridge
  digitalWrite(H_POS, LOW);
  digitalWrite(H_NEG, LOW);
  //Short pause to eliminate shoot-through
  delay(1);
  //Enable desired direction
  if (direction == true) {
    digitalWrite(H_POS, HIGH);
  }
  if (direction == false) {
    digitalWrite(H_NEG, HIGH);
  }
}
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

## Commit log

2021-01-06 Added new devices to library and Rev O.2 files
    [Transconductance Card.brd, Transconductance Card.sch]
2021-01-12 Added/connected new ADC & DAC to schematic; still unrouted on board
    [Transconductance Card.brd, Transconductance Card.sch]
2021-01-18 Added Card Tester Files
    [Rev A (Daughter Board).brd, Rev A (Daughter Board).sch, Rev A (Main Board).brd, Rev A (Main Board).sch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]
2021-01-25 Made bypass capacitor-diode thing symmetrical
    [Transconductance Card.brd]
2021-02-06 Partial Board Routing
    Need to finish routing power and update schematic power/GND symbols to be consistent with new convention
    [Transconductance Card.brd, Transconductance Card.sch]
2021-02-07 Routing Complete
    Still need to heat sink main fet and clean silk screen
    [Transconductance Card.brd]
2021-02-09 Board Routing Finished
    Need to clean up silkscreen still
    [Transconductance Card.brd, Transconductance Card.sch]
2021-02-13 Cleaned up silk screen
    [Transconductance Card.brd]
2021-02-14 Created BOM for JLCPCB Assembly
    [JLC BOM.xlsx]
2021-03-11 Update BOM
    [JLC BOM.xlsx, JLC PNP.xlsx, Transconductance Card.brd]
2021-05-26 Added Test Rig Arduino code

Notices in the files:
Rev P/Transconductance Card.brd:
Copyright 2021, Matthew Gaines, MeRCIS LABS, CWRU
